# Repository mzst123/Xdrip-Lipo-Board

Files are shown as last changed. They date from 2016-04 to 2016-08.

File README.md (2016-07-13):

# Xdrip Lipo Bluetooth Board PCB
Xdrip on a printed circuit board!

The design files are in the folder ["Eagle PCB Files"](https://github.com/mzst123/Xdrip-Lipo-Board/tree/master/Eagle%20PCB%20Files)

Or you can order the PCB directly [here](https://oshpark.com/shared_projects/IuYnoGB9)

For other versions of this project check out the folder ["Other Versions"](https://github.com/mzst123/Xdrip-Lipo-Board/tree/master/Other%20Versions)

If you can't solder this board and need help send me an email and im sure we can figure something out. My e-mail address is my github username at gmail.com

## Features:

- The board uses a MAX1811 battery charging ic
- Both Xbridge & Xdrip circuit support, selectable via a switch
- Battery can be soldered directly on the PCB (2.54mm header) or via a JST-2 connector (2mm pitch)
- Charging Status LED (On = charging; off = full)

## Components:

- 3x 1206 SMD Resitors (150Ω, 10kΩ, 27kΩ)
- 2x 1206 SMD Capacitor 10μf
- 2x micro switch MSK-12C02
- 1x 1206 Red LED (any led should work)
- 1x micro usb socket (ebay id: 121829362799)
- 1x MAX1811 lithium charger IC
- 1x [JST-2 connector 2mm pitch](https://www.sparkfun.com/products/8612) (optional - your battery needs to have the mating connector - sparkfun sells compatible batteries, or buy the connector separately and crimp it on your battery)
- 1x HM-11 Bluetooth V4.0 Transceiver BLE Module (I got the one from fasttech)
- 1x Polulu Wixel
- 1x LiPo/Li-ion Battery (I recommend using a LiPo battery)

Attention! The MAX1811 Charger IC is set to 500mah. Only use a battery with more than 500mah.

I source most of my components from eBay because of the free shipping. Here are some example links but consider that the prices change daily and shipping depends on where you are located:
- [Resistors](http://www.ebay.com/itm/100pcs-1-4W-watt-1206-SMT-SMD-Chip-Resistor-from-0-ohm-to-10M-ohm-1-/252380762812?var=&hash=item3ac310d2bc:m:msXv_-i2Opl1RPDANdY3cMw)
- [Capacitors](http://www.ebay.com/itm/12pcs-1206-smd-tantalum-capacitor-16v-10uf-106-10-3216-a-type-ic-diy-develop-d1-/331840663464?hash=item4d433eafa8:g:MpYAAOSwubRXFXfc)
- [Micro Switch](http://www.ebay.com/itm/20-pcs-MSK-12C02-Mini-SPDT-1P2T-Slide-Switch-On-Off-SMD-7-Pin-For-MP3-MP4-/161857451517?hash=item25af74b5fd:g:e1IAAOSwl9BWHbT4)
- [Red Led](http://www.ebay.com/itm/10-x-1206-RED-Super-Bright-LED-Chip-SMD-SMT-Bulb-Lamp-Light-High-Brightness-RoHs-/191231419928?hash=item2c8647e618:g:O3sAAOSw9N1Vo3OF&vxp=mtr)
- [micro usb socket](http://www.ebay.com/itm/2015-New-10Pcs-Micro-USB-B-Female-5Pin-SMT-Socket-Connector-Hot-Sale-MO-/401091696043?hash=item5d62ed95ab:g:R2kAAOSwDNdVpfv5)
- [Max1811](http://www.ebay.com/itm/1PCS-USB-LI-CHARGER-IC-MAXIM-SOP-8-MAX1811ESA-MAX1811ESA-MAX1811ESA-T-/272041007390?hash=item3f56e8591e:g:rx0AAOSwAYtWPgb~)
- [LiPo battery](http://www.ebay.com/itm/3-7V-850mAh-Lipo-Polymer-li-ion-Battery-703040-for-cell-phone-Camera-DVD-GPS-PAD-/111909510772?hash=item1a0e539e74:g:FAoAAOSwFNZWxojb)
- [Bluetooth module(Fasttech)](https://www.fasttech.com/product/1740900-hm-11-bluetooth-v4-0-transceiver-ble-module)

## PCB Assembly:

Everything is labeled on the PCB. The components are large enough to be soldered by hand, the trickiest for me was the micro usb socket. But if you use a hot air rework station (40$ on ebay) it should be very easy.

Here is a video how-to:

IMAGE ALT TEXT HERE (http://www.youtube.com/watch?v=SYGwYvehjtA)

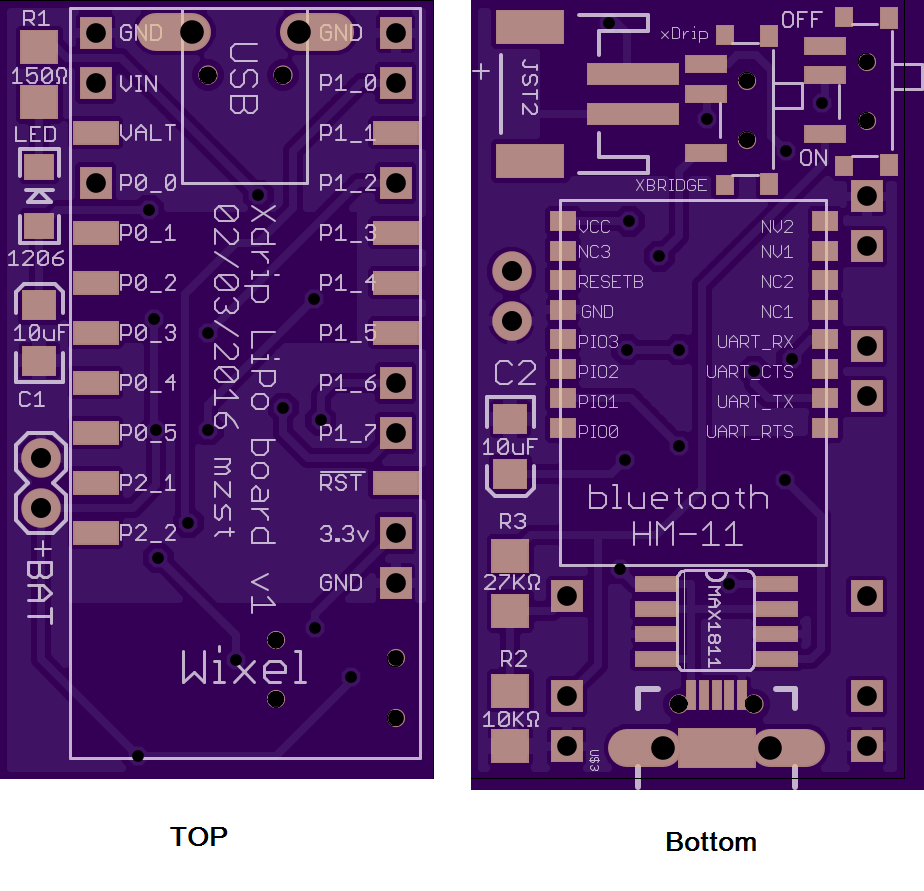
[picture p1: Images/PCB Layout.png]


## Schematics:

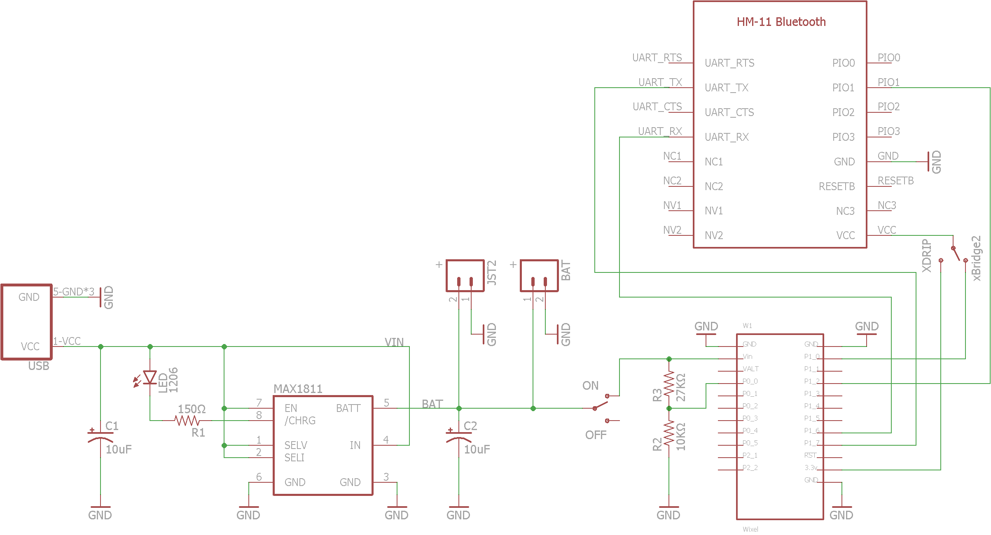
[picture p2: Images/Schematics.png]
Schematics


## Software:
For the Wixel software i recommend [xBridge](https://github.com/jstevensog/wixel-sdk/tree/master/apps/xBridge2) from [John] (https://github.com/jstevensog). Just download the .wxl file and load it to the wixel. There are many advantages of xBridge, for example you don't have to re-compile the program to change transmitters because you can set it inside the xDrip app, improoved power saving features, battery level estimate, etc...

[Here](https://github.com/StephenBlackWasAlreadyTaken/xDrip/wiki/xdrip-beta) you can download the latest xDrip android app.

## 3D Enclosure:

I made an enclosure, however it still has to be improved. To further reduce space, the JST-2 connector is not used in this design. In the future I might add one with JST-2 support. The battery compartment should fit an 850mah Lipo Battery (7x30x40mm). For more information and to download the .STL files go to the ["Enclosure"](https://github.com/mzst123/Xdrip-Lipo-Board/tree/master/Enclosure) Folder.
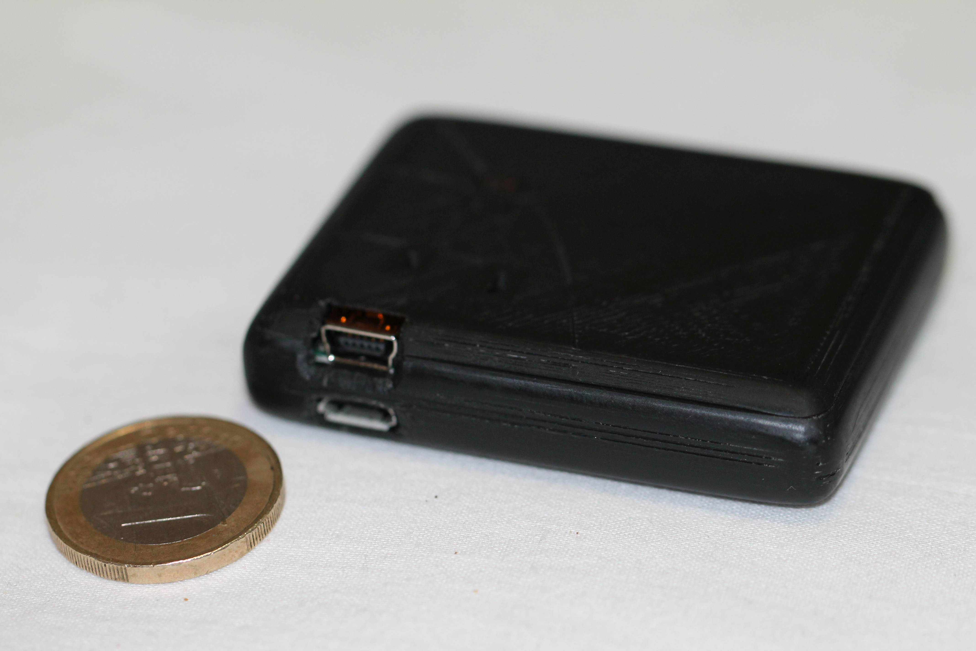
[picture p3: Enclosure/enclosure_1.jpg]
Enclosure


## Pictures:

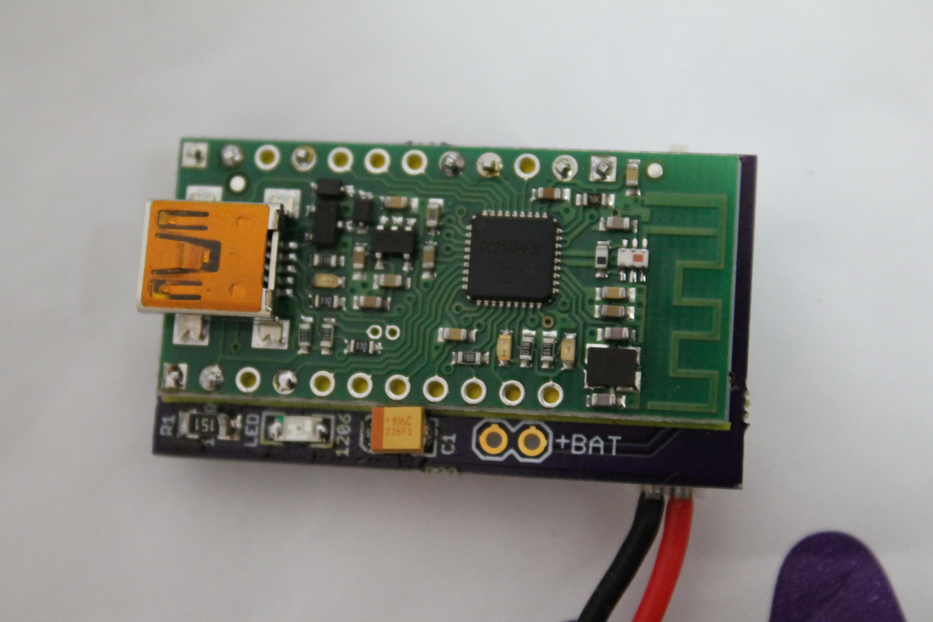
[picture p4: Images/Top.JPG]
Top View

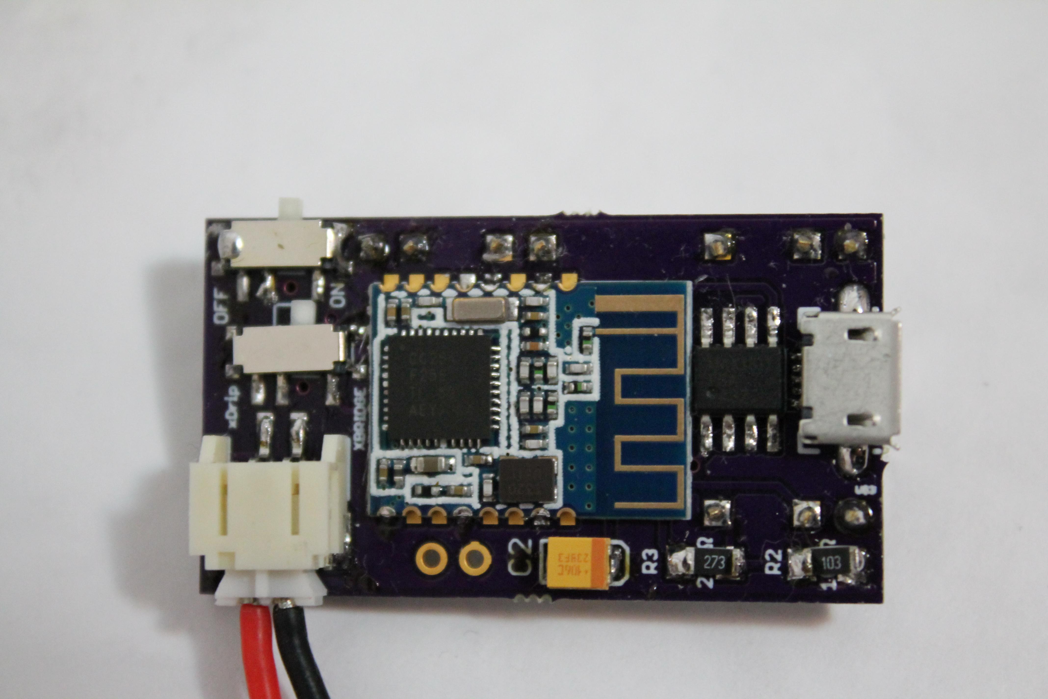
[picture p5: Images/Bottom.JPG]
Bottom View

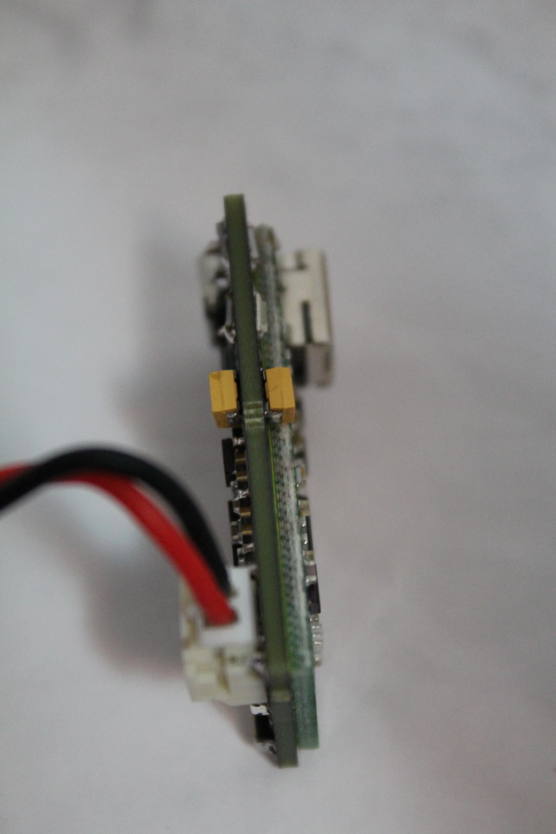
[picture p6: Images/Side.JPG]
Side View

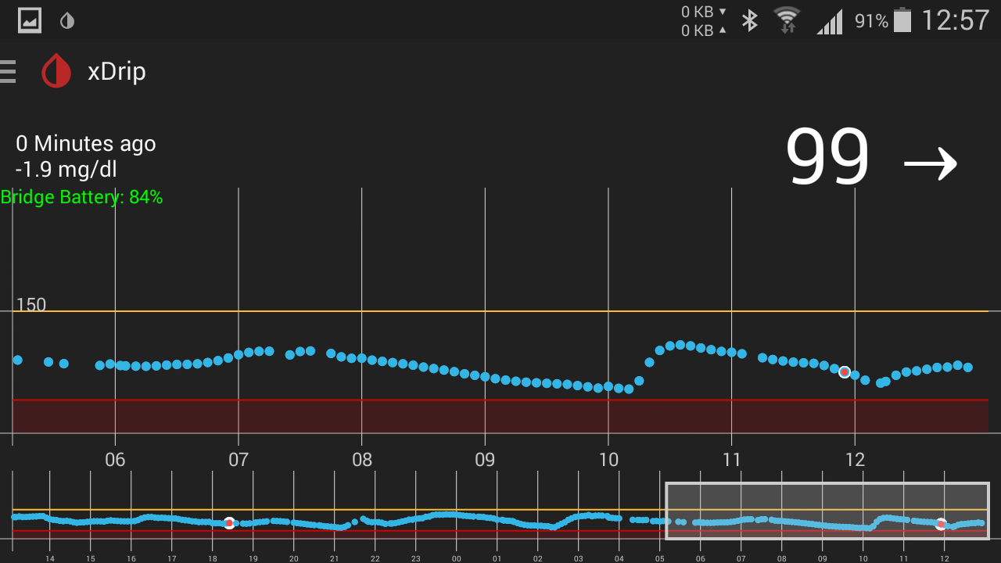
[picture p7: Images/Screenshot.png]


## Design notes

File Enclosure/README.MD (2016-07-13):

I made an enclosure, however it still has to be improved. To further reduce space, the JST-2 connector is not used in this design. In the future I might add one with JST-2 support. The battery compartment should fit an [850mah Lipo Battery](http://www.ebay.com/itm/3-7V-850mAh-703040-Lipo-Polymer-li-ion-Battery-for-cell-phone-Camera-DVD-GPS-PAD-/121844114909?hash=item1c5e79a5dd:g:LCwAAOSwUdlWdSaa) (7x30x40mm). 
I printed the parts on www.3dhubs.com for around 5€ shipped. The material used was PLA, but ABS is probably better.
Here are some pictures of the current progress:

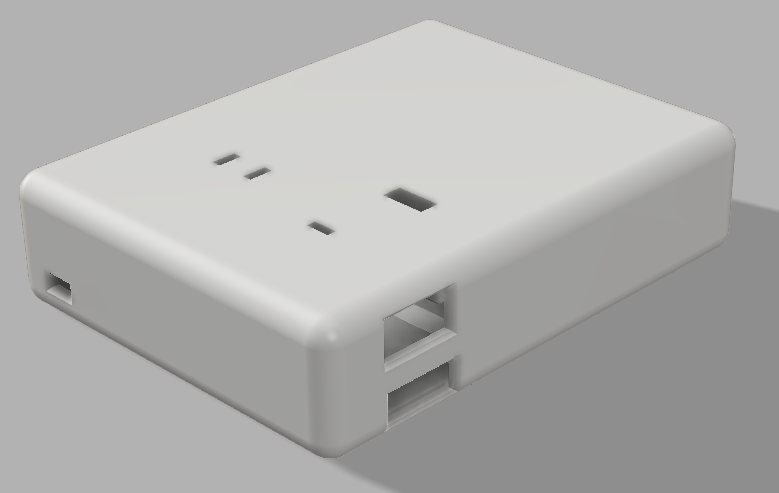
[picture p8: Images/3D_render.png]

Enclosure
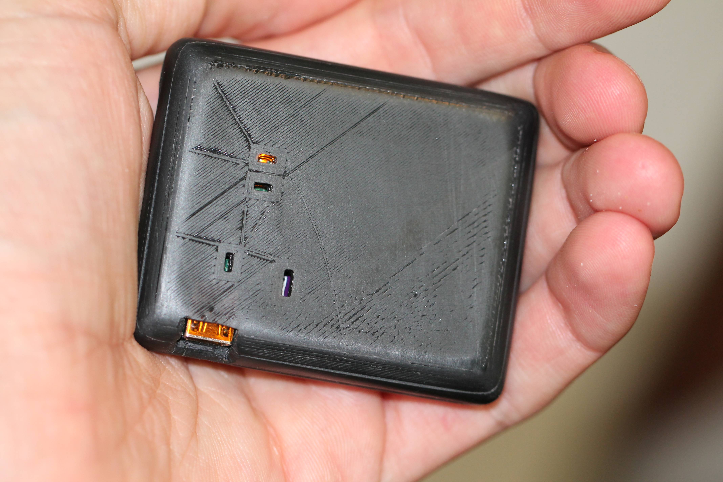
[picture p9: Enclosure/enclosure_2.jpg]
Enclosure

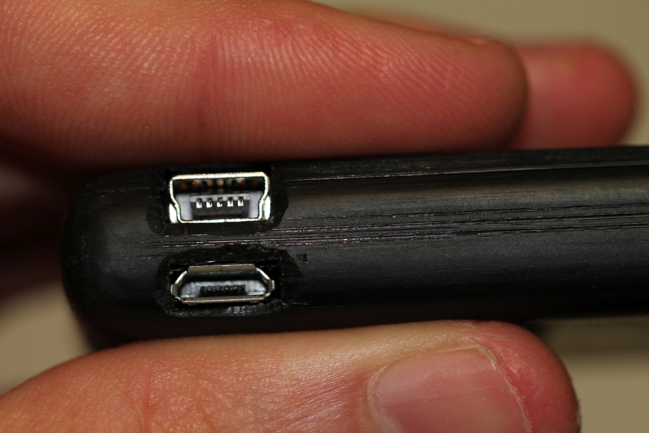
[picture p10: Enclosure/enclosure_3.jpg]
Enclosure

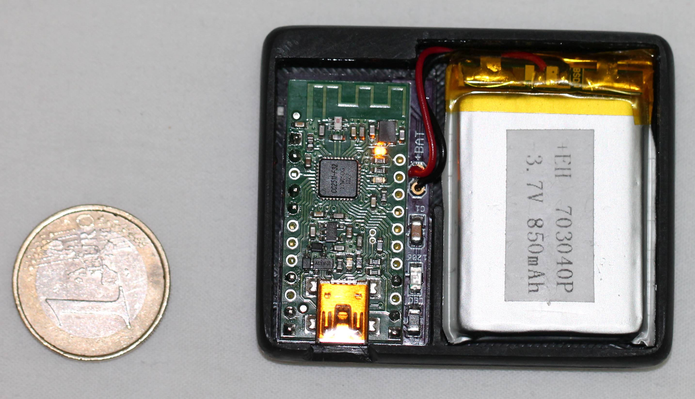
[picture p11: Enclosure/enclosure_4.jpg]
Enclosure


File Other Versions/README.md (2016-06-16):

# Other Versions

Here you will find other versions of the project.
- Currently there is only one for the [GSM/Parakeet Project](https://github.com/mzst123/Xdrip-Lipo-Board/tree/master/Other%20Versions/GSM-Parakeet)

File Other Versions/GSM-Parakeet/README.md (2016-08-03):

# GSM / Parakeet Version

# Tested & Works!
To order the PCB click [here](https://oshpark.com/shared_projects/pyIarV64).

This version uses a GSM module (SIM800L) instead of bluetooth. Check the [Parakeet project](https://jamorham.github.io/) for more info.

I had to switch to the TP4056 Charging IC because it has more power and is cheaper.

## Features:

- The board uses a TP4056 battery charging ic with a maximum charging power of 1000mA
- SIM800L Module sends the CGM data directly to the cloud
- Charging Status LED, Red = charging; Green = Full
- 4 ways to connect the battery: 
- - [JST-2 (sparkfun batteries, 2mm pitch)](https://www.sparkfun.com/products/341)
- - [JST-XH (ebay batteries, 2.54mm pitch)](http://www.ebay.com/itm/231387564843?_trksid=p2057872.m2749.l2648&ssPageName=STRK%3AMEBIDX%3AIT)
- - [2.54mm pitch screw-in connector](http://www.ebay.com/itm/2pcs-2-Poles-2-Pin-2-54mm-0-1-PCB-Universal-Screw-Terminal-Block-Connector-/262007114779?hash=item3d00d74c1b:g:5OIAAOSwPcVVwJQX)
- - Solder the wires directly

## Changelog
rev.1.0 - added JST-XH footprint, improoved pcb traces and vias

rev.0.9 - fixed SIM800L footprint, improoved pcb traces and vias

rev.0.8 - first version ready to manufacture

# Components

Most can be sourced from eBay

- SIM800L GSM Module
- 1x Polulu Wixel
- TP4056 Li Charging IC
- 2x 10μf Capacitors
- 1x 1.2kΩ Resistor (RPROG - 1.2kΩ=1000mA - Depends on Charging current - Check table below)
- 2x 330Ω Resistor
- 2x 1206 LED (1 Red and 1 Green)
- 1x [Micro USB Connector Female 4Legs](http://www.ebay.com/itm/10Pcs-Micro-USB-Type-B-Female-Socket-4-Vertical-Legs-For-Solder-Connectors-/351570406777?hash=item51db3aad79:g:UUwAAOSwu-BWOscw)
- 1x micro switch MSK-12C02
- 1x LiPo/Li-ion Battery (I recommend using a LiPo battery)
- 1x [JST-2 connector 2mm pitch](https://www.sparkfun.com/products/8612) (optional - your battery needs to have the mating connector - sparkfun sells compatible batteries, or buy the connector separately and crimp it on your battery)
- 1x JST-XH 2-pin connector (optional - only if your battery has this type of connector or you plan on crimping your own)

# Setting the charging current

You can individually set the charging current. Just change the RPROG resistor to the value you want.
The charging Current should be set dependent on the battery used. Always use a charging current equal or lower than the battery capacity.

|RPROG (kΩ)|IBAT(mA)| 
|:--------:|:------:|
|10        |130     |
|5         |250     |
|4         |300     |
|3         |400     |
|2         |580     |
|1.66      |690     |
|1.5       |780     |
|1.33      |900     |
|1.2       |1000    |

## Schematics:

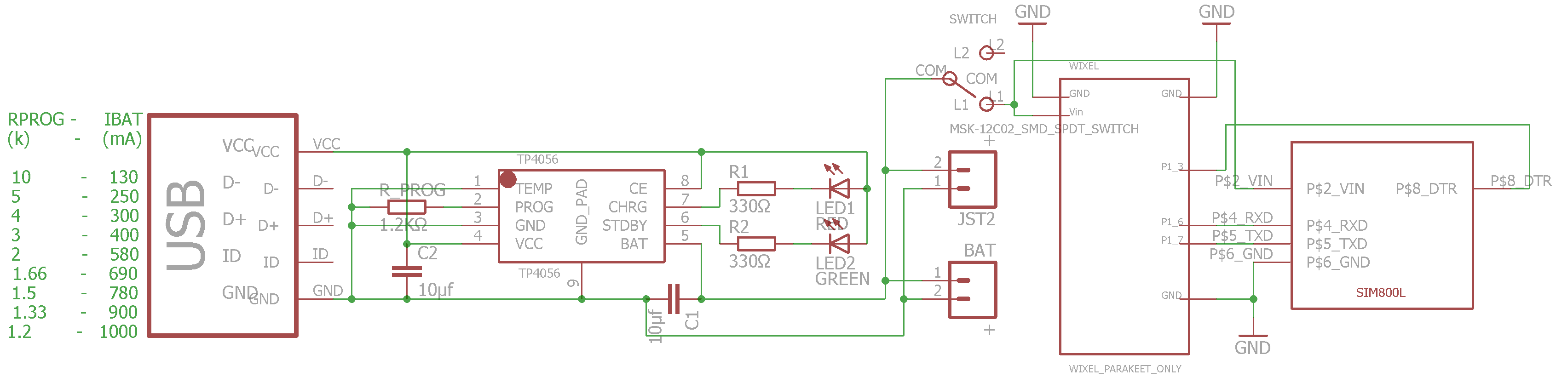
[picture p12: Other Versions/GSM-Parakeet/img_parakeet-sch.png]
Schematics


## Pictures:

Top View

Bottom View

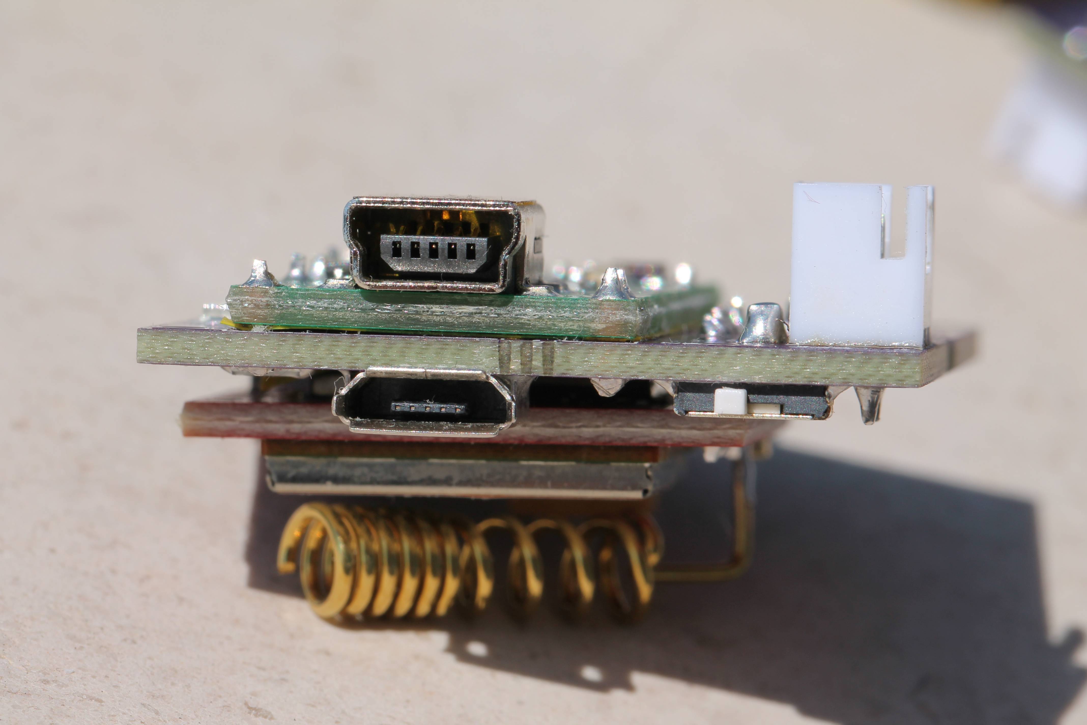
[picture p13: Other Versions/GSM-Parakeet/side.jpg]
Side

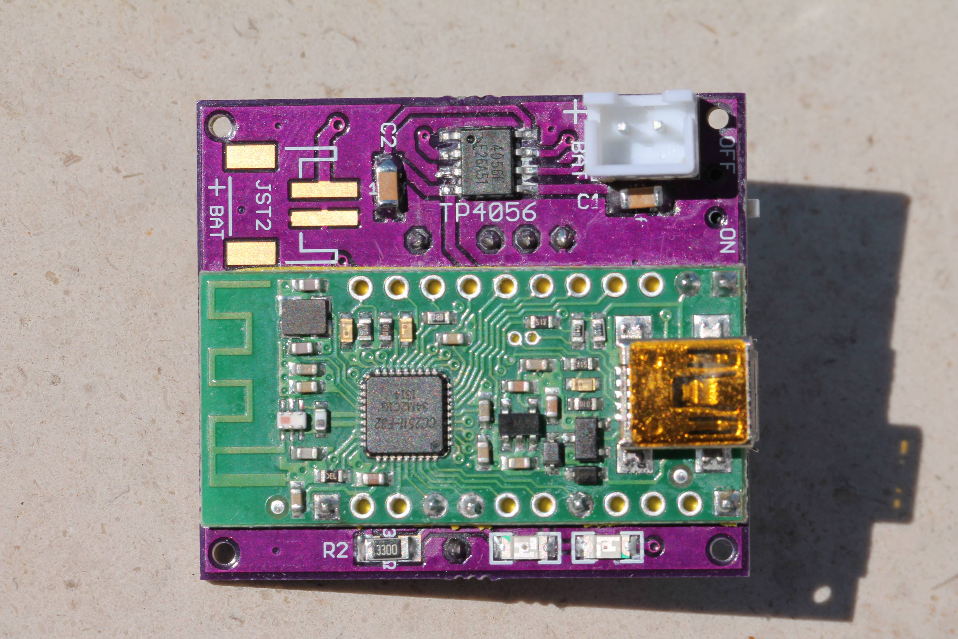
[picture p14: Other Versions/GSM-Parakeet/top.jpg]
Top

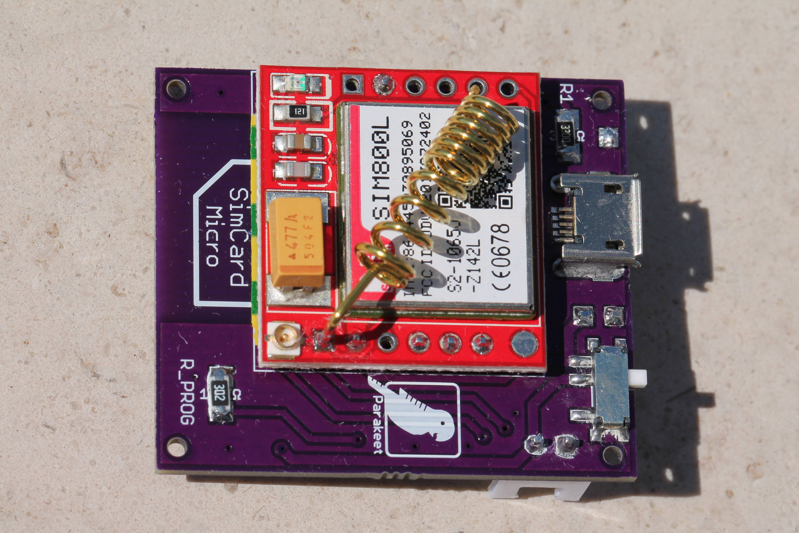
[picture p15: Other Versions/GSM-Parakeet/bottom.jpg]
Bottom

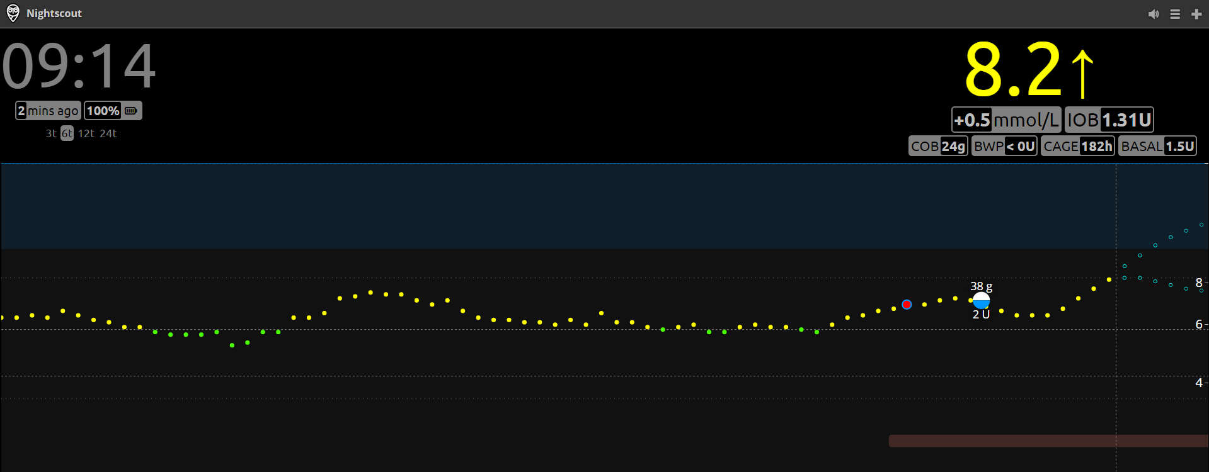
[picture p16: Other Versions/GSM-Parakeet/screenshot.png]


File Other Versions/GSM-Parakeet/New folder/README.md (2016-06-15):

# GSM / Parakeet Version

# Experimental Version - has not been tested yet
To order the PCB click [here](https://oshpark.com/shared_projects/lI7P3ltc).

This version uses a GSM module (SIM800L) instead of bluetooth. Check the [Parakeet project](https://jamorham.github.io/) for more info.

I had to switch to the TP4056 Charging IC because it has more power and is cheaper.

# Components

- SIM800L GSM Module
- 1x Polulu Wixel
- TP4056 Li Charging IC
- 2x 10μf Capacitors
- 1x 1.2kΩ Resistor (RPROG - 1.2kΩ=1000mA - Depends on Charging current - Check table below)
- 2x 330Ω Resistor
- 2x 1206 LED (1 Red and 1 Green)
- 1x Micro USB Connector Female 4Legs
- 1x micro switch MSK-12C02
- 1x LiPo/Li-ion Battery (I recommend using a LiPo battery)
- 1x JST-2 connector (optional - your battery needs to have the mating connector - sparkfun sells compatible batteries, or buy the connector separately and crimp it on your battery)

# Setting the charging current

You can individually set the charging current. Just change the RPROG resistor to the value you want.
The charging Current should be set dependent on the battery used. Always use a charging current equal or lower than the battery capacity.

|RPROG (kΩ)|IBAT(mA)| 
|:--------:|:------:|
|10        |130     |
|5         |250     |
|4         |300     |
|3         |400     |
|2         |580     |
|1.66      |690     |
|1.5       |780     |
|1.33      |900     |
|1.2       |1000    |

## Schematics:

Schematics

## Pictures:

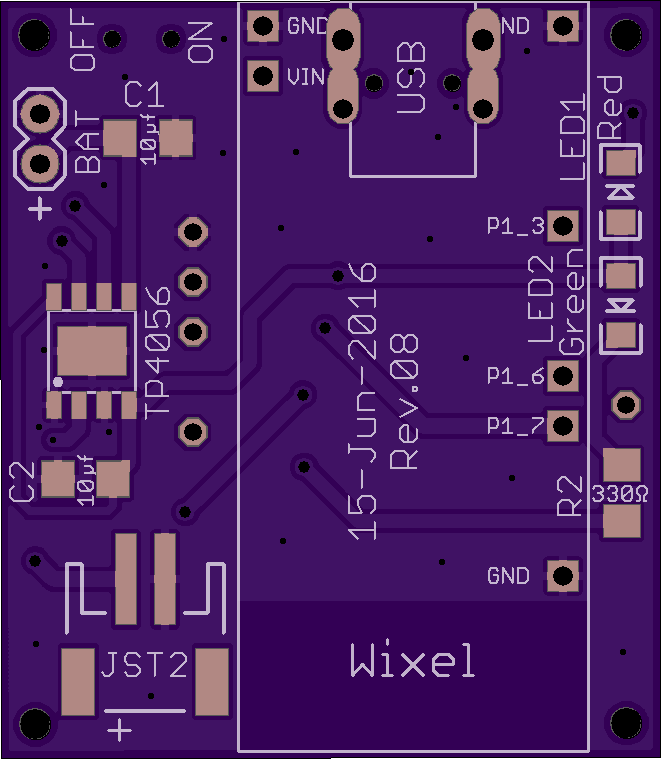
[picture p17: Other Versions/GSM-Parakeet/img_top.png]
Top View


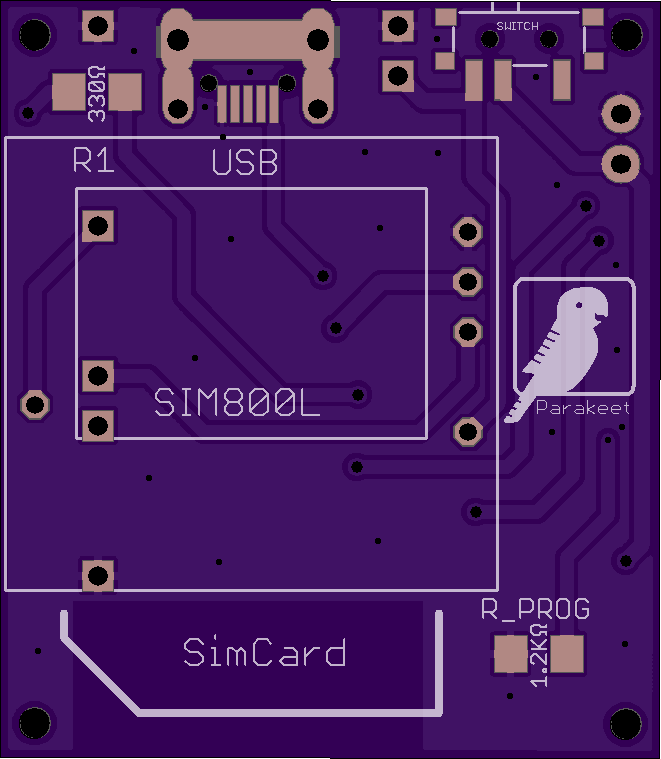
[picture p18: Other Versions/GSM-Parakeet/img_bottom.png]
Bottom View


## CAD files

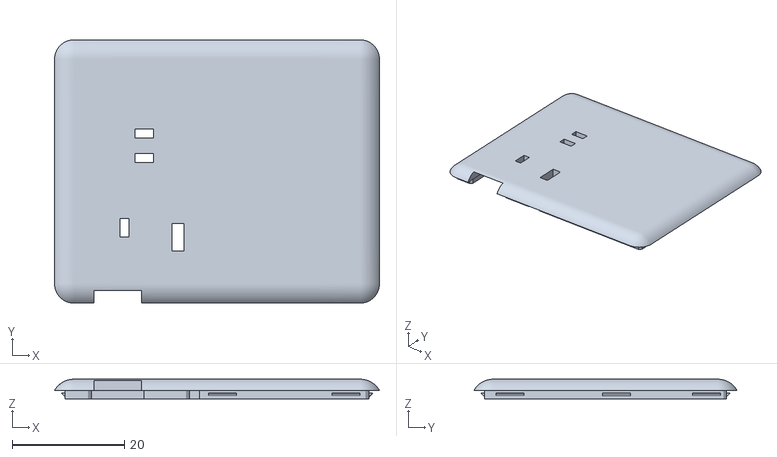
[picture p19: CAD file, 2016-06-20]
Enclosure/STL files/Top.stl
57.9 x 46.9 x 3.50

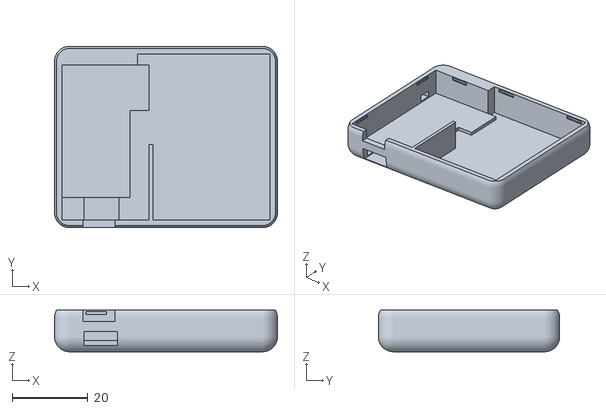
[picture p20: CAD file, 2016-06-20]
Enclosure/STL files/Bottom.stl
59.0 x 48.0 x 11.0

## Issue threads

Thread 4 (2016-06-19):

### ISSUE TITLE
GSM PCB

### ISSUE THREAD

**Issue by runeron** [mzst123/Xdrip-Lipo-Board#4]
First of all, thank you for this; excellent having a PCB to solder the components on.

Now that I have a working BLE receiver, I am planning to create a GSM receiver/[Parakeet](https://github.com/jamorham/wixel-xDrip/blob/parakeet-gsm-modem/README.md). What are the chances of you creating a modified version of this PCB where the HM11 is replaced by the SIM800L GSM module?

I would do it myself, but then I have to teach myself HOW first...

**Comment by mzst123** [comment]
Hi, it sure seems very easy. The only problem is that there is no footprint available. I do not have a SIM800L module. Can you measure the holes of the module and make a drawing? Then I can copy it into the program.
I need to do something like this so only the distances of the holes and the outline of the module are relevant. Regards
![tp4056 module](https://cloud.githubusercontent.com/assets/16510934/15784499/b0c4566e-29aa-11e6-8a05-74ac352b6b8c.png)

**Comment by runeron** [comment]
Outer dimension of module: 2.5 cm x 2.3 cm (Thickness is x 0.7 cm). The holes are made for pin headers w/2.5 mm pitch. Drawing is best effort..
![sim800l](https://cloud.githubusercontent.com/assets/3177490/15791790/bd39378c-29d9-11e6-98f1-7337ec182b2b.png)
Not sure how it would be solved to have it on the PCB, but since there are components on both sides, maybe just have holes for the 6 x 1 & 5 x 1 pin headers (2.5 mm pitch) on each side of the SIM800L board?

**Comment by mzst123** [comment]
Thanks i will see what i can come up with. Only one measurement is missing: the distance between the hole and the edge of the PCB.
![untitled](https://cloud.githubusercontent.com/assets/16510934/15802480/a504b286-2aab-11e6-95c0-6b06b9b27a35.png)

**Comment by runeron** [comment]
Nice.. It's 1,5 mm as far as I can measure.

Edit: The measurements in my earlier sketch was from center-hole. Just thought I'd mention it

**Comment by mzst123** [comment]
Hi, I just made this draft. Please print this out on an sheet of A4 paper. If you can, use a laser printer on maximum resolution setting. Then place the module on top an check if it fits. You can also stick the header pins into the paper and see if they fit. 
The sim tray is on the back (in contact with the paper).
Thanks
[SIM800L-.pdf](https://github.com/mzst123/Xdrip-Lipo-Board/files/303821/SIM800L-.pdf)

**Comment by runeron** [comment]
Amazing! I will try it out as soon as I get back from work today.

I did notice a potential challenge yesterday, though.. It doesn't look like the SIM800L will work with the 3.3V from Wixel (requires 3.4V~4.4V & 2A at peak):

![image](https://cloud.githubusercontent.com/assets/3177490/15887249/8a6cdba2-2d61-11e6-82c5-7e904d6ce6e0.png)

I did all the connections on my breadboard; just replacing the HM11 w/GSM, and was not able to communicate with it. After doing som more reading, it appears the Wixel is not able to wake up the SIM module.

I tried connecting the SIM800L directly to the powersource (first 500mAH, 3.7V Li Po (25C), then 2400mAH, 3.7V Li Ion battery) with no success. I think I might need another powersource, and I also think the SIM800L needs to be powered directly from source; I guess this would require additional modifications of the PCB.

It COULD be the simcard (provider/defect/etc), but ran out of time yesterday; I was also struggling with figuring out the meaning of the different the LED statuses I got. Will try more today if I manage to find the time, and will try powering w/batteries as suggested in jamorham's parakeet guide.

It is a bit more work than I thought.. Still; if you make the Eagle model of SIM800L that would be fantastic.. Then I can eventually try and make a PCB myself if this is too much work for you :)

**Comment by runeron** [comment]
Hi, and sorry for the delay!

I matched up the pins as best I could, and it looked like it was a perfect fit.

I've had a look at your eagle files, and I can order the parts and try this out whenever you feel it is ready. No problem if it doesn't work on the first try.

My only issue is deliverytime of PCB boards; I might need to find a quicker way of getting them made.

**Comment by mzst123** [comment]
Perfect. I made the board as a test. I still have to move some components for better access to the simcard, as i don't know how much space there will be to insert it. During next week it will be ready ;). I changed some of the components (lessons learned from the old board). Can you solder the smaller components?
If not, i could help you assembling the boards. I bought a hot air rework station, so let me know.

**Comment by runeron** [comment]
I did struggle a bit with a few components on the last board, but I am waiting for some solder paste now; hoping this will help..

Not sure how you could assist in assembling, as I live in Norway. Otherwise that would be great:)

**Comment by mzst123** [comment]
Well I could order the parts, assemble the boards and mail them to you. Its not a problem for me, however it will take a little longer.

**Comment by runeron** [comment]
Wow. That would be amazing.. I can transfer money for parts/work via paypal or whatever you prefer, if you pm me the details.

Edit: removed

Not sure how that is possible on github, so will leave my email here for now. :)

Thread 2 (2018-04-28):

### ISSUE TITLE
Little Help Needed here in Canada

### ISSUE THREAD

**Issue by Tatt2edone** [mzst123/Xdrip-Lipo-Board#2]
I have ordered the boards from OSH Park, I am currently looking for all the parts needed, my question involves the micro switches, are they a must? I currently have an xDrip Wireless Bridge built, there are no switches, its always on. I get the on/off switch option, but what is the difference between xdrip circuit and xbridge circuit? 

I am sorry if this is a dumb question, just don't want to mess this up.

**Comment by mzst123** [comment]
Hello, switches are not a must, but I have them because if you choose to solder on the battery permanently, you have no way to reboot or turn off the device, for troubleshooting etc... 
If you don't want to use the switches, just bridge the contacts with a little wire and solder.
There are two circuits, wich vary only slightly. 
The original **xDrip** project used a circuit, wich was then further improved by John (jstevensog) and called **xBridge**.
He changed the [Wixel Program](https://github.com/jstevensog/wixel-sdk/tree/master/apps/xBridge2) to perform better and more efficient, and to show an approximate battery level value. You also don't have to compile the program each time you switch transmitters, because you can set the Transmitter ID from within the xDrip app. You can use this Wixel Program with both circuits, but the power saving features only work with the xBridge circuit.
Its up to you wich one you prefer, and with the switch you can easily test wich one works better for you. Another advantage is that the xBridge Wixel Program continues to be updated and improved to this day.
I personally use the xBridge circuit. 
As a side note, make sure you buy the exact micro-usb socket type as indicated, as there are many different versions and not all of them fit the layout perfectly.

Regards and good luck, if you have any questions ask away.

**Comment by Tatt2edone** [comment]
Thanks for the reply, I used the xDrip UK site to auto compile the wixel program for xDrip, but I think I will look into xBridge, 
Is this usb the correct one?

http://www.digikey.ca/scripts/DkSearch/dksus.dll?Detail&itemSeq=197088528&uq=635986860270805947

This company has all the parts listed and are in Canada so I don't have to worry about crazy exchange rates and long shipping times.

One last thing for now, I checked out the xBridge github, I am very new to this stuff, I am on my own building this stuff for my wife and just want to get it right for her. Can I just download the wixel file, reprogram my current xDrip box?

We are using the most current beta of xDrip, will it recognize the xBridge wixel program?

**Comment by mzst123** [comment]
Hi, unfortunately the link doesn't return a valid result. [This one](http://www.digikey.ca/product-detail/en/amphenol-fci/10118192-0001LF/609-4613-2-ND/2785387) should work, however it is not the one i used (cant find it on this site). The one i used has two little plastic legs that will fit the holes in the PCB, but for functionality it is not important, it just makes placing the part easier. If you are going to Reflow the board it doesn't matter, both will work fine.
About the xBridge, yes. Just download the .wxl file and load it on to the wixel. It should set itself up in a few minutes, watch the LEDs blinking, it is described in the PDF. You don't have to do anything. Just pair the device with the phone (I think HM-11 default pin is 000000 (six zeroes)) and xDrip should recognize the wixel just fine. Then enter the Transmitter ID. That's it. Regards

**Comment by Tatt2edone** [comment]
Hey, back again, I talked with digi-key about getting a jst-2 connector, apparently there are many variations in spacing for the pins. Do you remember what the spacing of the one you used? What type was it, right angle, flat (if there's such a thing) etc?

Thanks for your patience and help, I received shipping notice from OSH that the boards are on their way.

**Comment by mzst123** [comment]
Hey, [This is the one i used](https://www.sparkfun.com/products/8612) but i bought it from element14 as i am from europe. I bought all the other components from eBay with free shipping. Took over a month to arrive though. This connector is not strictly necessary as you can solder the battery directly on board if you can't source it. It is also quite expensive, that's why i left it optional. Digikey is very expensive on shipping. Regards
Edit: I forgot to add, they are the 2mm (header, smt) variant. Cheers

**Comment by mzst123** [comment]
I forgot to add, they are the 2mm (header, smt) variant. Cheers

**Comment by Tatt2edone** [comment]
Much appreciated! I will see what my area's supplier has. Cheers to you as well! DigiKey is only $8 shipping for all the parts I am ordering, everything needed in addition to what I have is there. I have 2 wixels, a bunch of hm-10 and a bunch of hm-11 on the way, I realize the hm-10 won't fit, but have them for old school xDrip builds in a pinch :)

**Comment by apabari** [comment]
Hello!  Tatt2edone, wondering -- do you have a parts list for the digikey order that you could post/share?  I'm also in Canada, and interested in ordering the components (and a board from OSHPark) -- just a little lost on the digikey website.

**Comment by apabari** [comment]
Just checking in!  Could anyone post the parts list for getting the components from digikey?

**Comment by mzst123** [comment]
Hey, its easier if you buy from eBay... lower prices because you can buy lower quantities... Didn't i send you a board some time ago? What happened?

**Comment by apabari** [comment]
I never received the board.  Lost our original e-mail thread so I didn't reach out again.  Do you have the tracking number? I'd love to try and find out what happened to it!

I ordered the components from e-bay and built one, but I'm pretty sure I ordered the wrong resistors and capacitors... it didn't work.  If you could point me at the product codes from digikey that would be great.  They do next day shipping and it's pretty inexpensive to order from them here in Toronto.

**Comment by mzst123** [comment]
So it was you. I wasn't sure. The board was returned to my address with a notice that it was delivered but not accepted. Im not sure if i still have the tracking number but it has probably expired anyway. Since you never reached out I forgot about it. I will look up the codes later today

**Comment by apabari** [comment]
That's really strange!  I am very disappointed to hear that.  If you could refund me the cost (less shipping, of course) I would really appreciate that as well.  Thanks for your help with finding the codes!

**Comment by mzst123** [comment]
Just sent you a refund! Here are some parts, if you need more help let me know:
[10KΩ resistor](http://www.digikey.pt/product-detail/en/yageo/RC1206FR-0710KL/311-10.0KFRCT-ND/731430)
[27kΩ Resistor](http://www.digikey.com/product-detail/en/yageo/RC1206FR-0727KL/311-27.0KFRCT-ND/731679)
[150Ω resistor](http://www.digikey.com/product-detail/en/yageo/RC1206JR-07150RL/311-150ERCT-ND/732170)
[10μf Capacitor](http://www.digikey.pt/product-detail/en/yageo/CC1206ZKY5V7BB106/311-1376-2-ND/2103114)
[LED](http://www.digikey.com/product-detail/en/kingbright/APT3216SURCK/754-1143-2-ND/1747542)

**Comment by apabari** [comment]
Thank you!  Just ordered the parts from Digi-Key.  Thanks so much for all of your continued help - hope this works out for me!

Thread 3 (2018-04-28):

### ISSUE TITLE
New to T1 & looking at getting set up

### ISSUE THREAD

**Issue by Deneil1983** [mzst123/Xdrip-Lipo-Board#3]
Morning I'm new to T1 Diabeties, my 5yr old daughter has been resently diagnosed. Be been trying to work out what's the best method for Xdrip while Mariella is at school. I've ordered the newest version of the PCB Xdrip board, wixel, HM11 but as far as anything else goes I haven't got a clue were or what there for. We're do I get the info to download the wixel? And could you post links were to get the rest of the components that I would need to get. I'm in the UK so anywere UK or Europe based would be a help xxx

**Comment by runeron** [comment]
Hello. I would suggest you read the following:
- [Nightscout](http://www.nightscout.info/)
- [xDrip](http://stephenblackwasalreadytaken.github.io/xDrip/)

Regarding the PCB blueprints posted here, they are for creating an additional/alternative Dexcom receiver. All components are listed on this site as well (and also the wiring diagram, for your question regarding the other components). It is marked on the PCB where each component goes. Personally I have used the following sites for ordering: eBay, SparkFun, HobbyTronics

NOTE: xBridge and xDrip are essentialy the same, but xBridge circuit has some additional functionality (at least that is how I understand it). Some of the "additional" components are only required if you use the xBridge setting (?).

My reasons for creating this board (still waiting for components):
- Monitor our 3 yr old (T1 for 6 months) even when he's in kindergarden/visiting others
- Use smartphones instead of the Dexcom receiver
- Uses "better" algorithm for calculating sender measurements, compared to the outdated Dexcom EU software

I would also sugges you check out the site listed below, which has instructions for creating a receiver to upload data to the "cloud" without need for an android phone:
- [Parakeet](http://jamorham.github.io/)

Best of luck!

**Comment by mzst123** [comment]
@runeron Yes that is exactly how it works. The only additional components the xBridge needs are two resistors to estimate battery level.

@Deneil1983 I have sourced almost all components from eBay, as the shipping is free (it takes a month to arrive from China or HongKong though). For example, for the LED, just go to `ebay.com` and enter `1206 Red LED`. Then you sort by `Price + Shipping: lowest first`and click on only show `Buy it now` results. Now scroll down a little until you find one result that you want, for example i got [this one](http://www.ebay.com/itm/10-x-1206-RED-Super-Bright-LED-Chip-SMD-SMT-Bulb-Lamp-Light-High-Brightness-RoHs-/191231419928?hash=item2c8647e618:g:O3sAAOSw9N1Vo3OF&vxp=mtr).
For $0.80 you get 10 Leds shipped to your house, no additional charges. Quite Cheap considering that on most other electronic websites you have to pay over 5€ in shipping. Now do the same process for all the other components. Here are some example links but consider that the prices change daily and shipping depends on where you are located (I live in Portugal). If you don't want to wait that long then order from a local supplier, for the UK i think Farnell/Element14 is good but expensive.
- [Resistors](http://www.ebay.com/itm/100pcs-1-4W-watt-1206-SMT-SMD-Chip-Resistor-from-0-ohm-to-10M-ohm-1-/252380762812?var=&hash=item3ac310d2bc:m:msXv_-i2Opl1RPDANdY3cMw)
- [Capacitors](http://www.ebay.com/itm/12pcs-1206-smd-tantalum-capacitor-16v-10uf-106-10-3216-a-type-ic-diy-develop-d1-/331840663464?hash=item4d433eafa8:g:MpYAAOSwubRXFXfc)
- [Micro Switch](http://www.ebay.com/itm/20-pcs-MSK-12C02-Mini-SPDT-1P2T-Slide-Switch-On-Off-SMD-7-Pin-For-MP3-MP4-/161857451517?hash=item25af74b5fd:g:e1IAAOSwl9BWHbT4)
- [Red Led](http://www.ebay.com/itm/10-x-1206-RED-Super-Bright-LED-Chip-SMD-SMT-Bulb-Lamp-Light-High-Brightness-RoHs-/191231419928?hash=item2c8647e618:g:O3sAAOSw9N1Vo3OF&vxp=mtr)
- [micro usb socket](http://www.ebay.com/itm/2015-New-10Pcs-Micro-USB-B-Female-5Pin-SMT-Socket-Connector-Hot-Sale-MO-/401091696043?hash=item5d62ed95ab:g:R2kAAOSwDNdVpfv5)
- [Max1811](http://www.ebay.com/itm/1PCS-USB-LI-CHARGER-IC-MAXIM-SOP-8-MAX1811ESA-MAX1811ESA-MAX1811ESA-T-/272041007390?hash=item3f56e8591e:g:rx0AAOSwAYtWPgb~)
- [LiPo battery](http://www.ebay.com/itm/3-7V-850mAh-Lipo-Polymer-li-ion-Battery-703040-for-cell-phone-Camera-DVD-GPS-PAD-/111909510772?hash=item1a0e539e74:g:FAoAAOSwFNZWxojb)

For the Wixel software i recommend [xBridge](https://github.com/jstevensog/wixel-sdk/tree/master/apps/xBridge2) from [John](https://github.com/jstevensog). Just download the .wxl file and load it to the wixel. There are many advantages of xBridge, for example you don't have to re-compile the program to change transmitters because you can set it inside the xDrip app. Regards

**Comment by Deneil1983** [comment]
Thank you for all your help, I think I've managed to get everything. Could you just double check these links to make sure there all correct before I go and buy them please?

https://www.ebay.co.uk/ulk/itm/121966808792 

https://www.ebay.co.uk/ulk/itm/391293464671 

https://www.ebay.co.uk/ulk/itm/361517418457 

https://www.ebay.co.uk/ulk/itm/321604978839 

https://www.ebay.co.uk/ulk/itm/261474884369 

https://www.ebay.co.uk/ulk/itm/191794514614 

https://www.ebay.co.uk/ulk/itm/151637924468

**Comment by mzst123** [comment]
Yes that looks good. Let me know when you finish it. Cheers

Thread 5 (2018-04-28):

### ISSUE TITLE
Parakeet

### ISSUE THREAD

**Issue by Deneil1983** [mzst123/Xdrip-Lipo-Board#5]
Hi have you had any joy getting the parakeet to work? I've ordered the parts but as yet not been able to older them all together, is there anyway you would be able to help me build the parakeet if I was to send you all the stuff. 

Thanks
Deneil

**Comment by mzst123** [comment]
Sure thing. It works. I can help you, no problem. Please contact me via e-mail

**Comment by Deneil1983** [comment]
Your a life saver, will email you now thanks

**Comment by Deneil1983** [comment]
Hi thank you so much for agreeing to help me get set up with the parakeet. What would be the best way for you to help me get set up? I send you what I already have or you make it and I cover the costs for materials? I'm ok with both suggestions.

Thanks once again 
Deneil xxx

Deneil Yates-Savage 💗

Wednesday, 3 August 2016, 2:16 pm +0100 from notifications@github.com  notifications@github.com:

**Comment by Deneil1983** [comment]
Hi can you send.me.your email address xxx

**Comment by mzst123** [comment]
Hi, i think it is easier if you send me what you already have.

**Comment by Deneil1983** [comment]
Email sent thank you so much

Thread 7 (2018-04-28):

### ISSUE TITLE
Enclosure - different size batteries?

### ISSUE THREAD

**Issue by whoiswes** [mzst123/Xdrip-Lipo-Board#7]
mzst123,

First, thank you for putting both the PCB and enclosure projects together - I have built 2 boards so far and they have performed fantasic!

I do however wonder if it would be possible to have additional enclosures designed for larger batteries.  Currently I'm using a 2000 mAh battery from adafruit in a tic-tac case.  It's functional, but larger.  I'd be happy to design a case around the larger battery size, but am unsure where to start in terms of design tools  I have zero 3D printing experience.

My apologies for putting this on the bug tracker as a discussion rather than an actual bug, but hopefully this will spawn some useful discussion, if nothing else.

Again, thank you so much for making this available

Wes

**Comment by mzst123** [comment]
Hi, i used the free program "Autodesk Fusion 360" to design the cases but im sure there are better ways to do it. It works but has some annoyances. I also had no experience in 3D design before. I made an updated version from the mistakes learned (but with same size battery) that i haven't published yet. The biggest problem I encountered was with the tolerances of the material/printer. Another issue was the closing mecanism which is not possible to do reliably with the material i used (PLA) so now i just close it with some adhesive tape.
I can upload the files if you want.
Regards

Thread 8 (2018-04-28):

### ISSUE TITLE
Version V2.1

### ISSUE THREAD

**Issue by d3xr** [mzst123/Xdrip-Lipo-Board#8]
Hi! Where I can find Xdrip PCB Lipo Board V2.1 files?

**Comment by mzst123** [comment]
Hi, the files are [here](https://github.com/mzst123/Xdrip-Lipo-Board/tree/master/Eagle%20PCB%20Files). you can also order them directly from [OSHPark](https://oshpark.com/shared_projects/IuYnoGB9). Regards

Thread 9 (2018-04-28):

### ISSUE TITLE
Help from an expert needed

### ISSUE THREAD

**Issue by Stef-M** [mzst123/Xdrip-Lipo-Board#9]
Hi,
i've read about this wonderful project, and am very interested.
I'd like to ask you if you have considered to sell one (eg if you have one more circuit).
Unfortunately I'm not so expert for realizing one from scratch.

Many thanks in advance.

Best regards :)

**Comment by mzst123** [comment]
Hi, I think I should still have one or two at home. I will check and let you know tomorrow. Regards

**Comment by mzst123** [comment]
Hi @Stef-M 
I just checked and i still have parts to build at least one. Only the Bluetooth module is missing, but i could order it for you. Let me know if you are still interested.
Regards

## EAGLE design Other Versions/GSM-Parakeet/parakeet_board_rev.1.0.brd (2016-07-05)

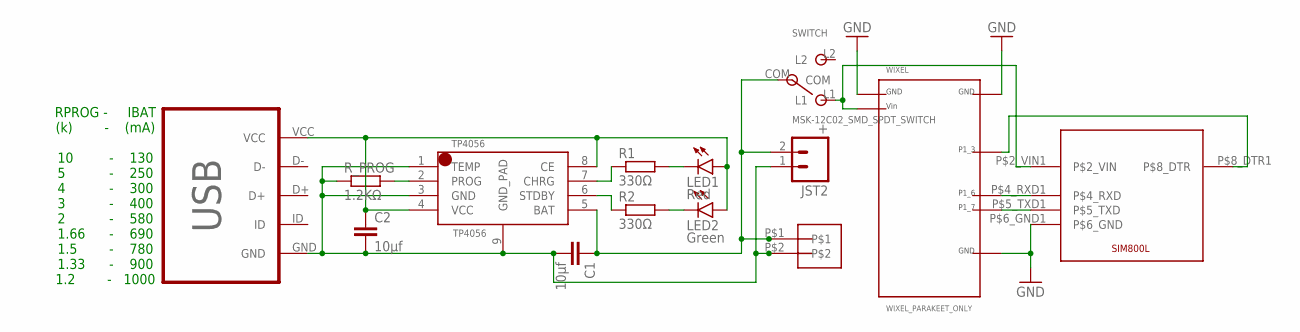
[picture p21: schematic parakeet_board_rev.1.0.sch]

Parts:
C1, C2: 10μf; C1206
JST2: +; JST-2-SMD
JST-XH: 2_PIN_JST-XH-B2B
LED1: Red; LED-1206
LED2: Green; LED-1206
R1, R2: 330Ω; R1206
R_PROG: 1.2KΩ; R1206
SIM800L: SIM800L_PARAKEET_ONLY
SWITCH: MSK-12C02_SMD_SPDT_SWITCH; MSK-12C02
TP4056: TP4056; SOP-8
USB: MICRO-USB-B; MICRO_USB_4_LEGS
WIXEL: WIXEL_PARAKEET_ONLY

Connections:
GND: C1.2, C2.2, JST2.1 (2), JST-XH.P$2, R_PROG.1, SIM800L.P$6_GND1 (P$6_GND), TP4056.1 (TEMP), TP4056.3 (GND), TP4056.9 (GND_PAD), USB.GND, WIXEL.P$1 (P$1-GND1), WIXEL.P$12 (P$12-GND2), WIXEL.P$23 (P$23-GND3)
unnamed: R_PROG.2, TP4056.2 (PROG)
unnamed: SIM800L.P$5_TXD1 (P$5_TXD), WIXEL.P$20 (P$20-P1_7)
unnamed: LED1.C, R1.2
unnamed: LED2.C, R2.2
unnamed: R1.1, TP4056.7 (CHRG)
unnamed: R2.1, TP4056.6 (STDBY)
unnamed: C2.1, LED1.A, LED2.A, TP4056.4 (VCC), TP4056.8 (CE), USB.VCC
unnamed: C1.1, JST2.2 (1), JST-XH.P$1, SWITCH.COM, TP4056.5 (BAT)
unnamed: SIM800L.P$4_RXD1 (P$4_RXD), WIXEL.P$19 (P$19-P1_6)
unnamed: SIM800L.P$2_VIN1 (P$2_VIN), SWITCH.L1, WIXEL.P$2 (P$2-VIN)
unnamed: SIM800L.P$8_DTR1 (P$8_DTR), WIXEL.P$16 (P$16-P1_3)

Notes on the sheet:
RPROG - IBAT (k) - (mA) 10 - 130 5 - 250 4 - 300 3 - 400 2 - 580 1.66 - 690 1.5 - 780 1.33 - 900 1.2 - 1000

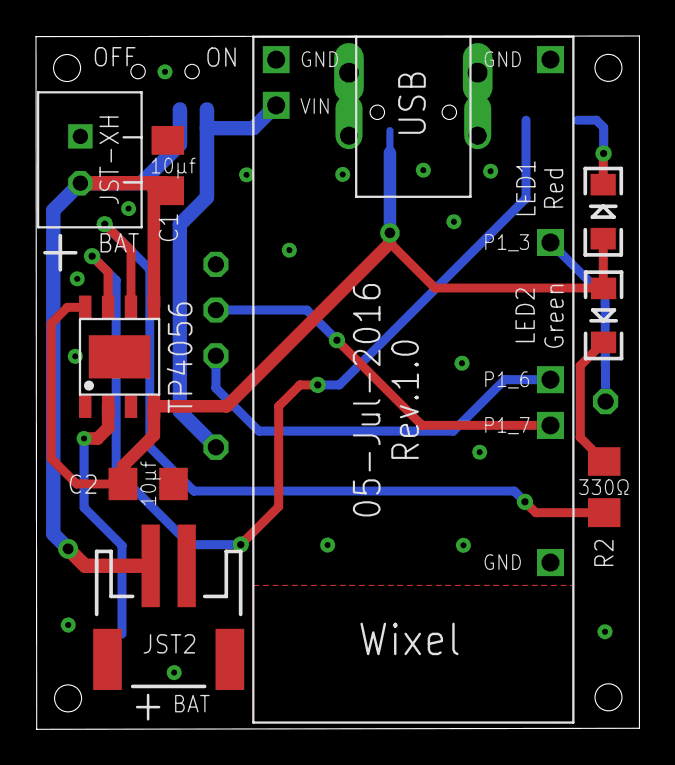
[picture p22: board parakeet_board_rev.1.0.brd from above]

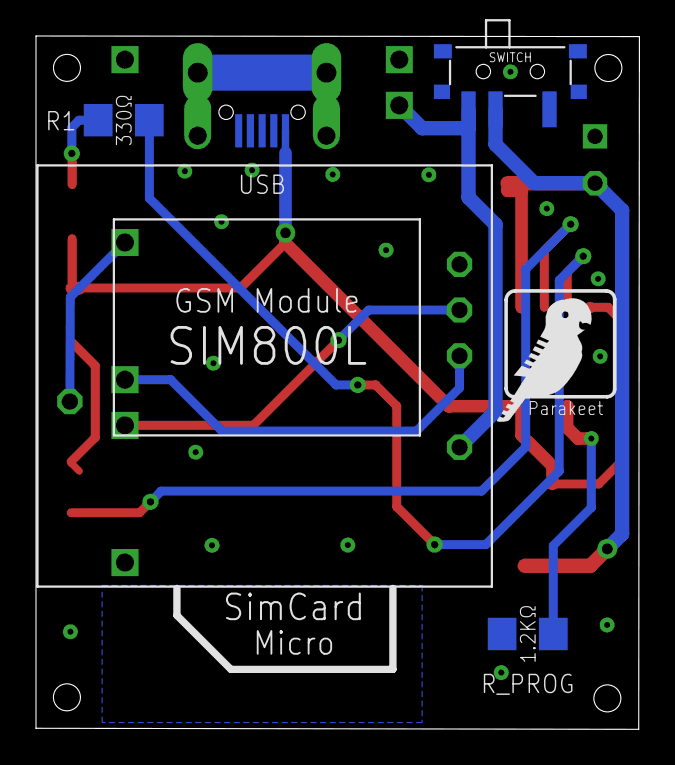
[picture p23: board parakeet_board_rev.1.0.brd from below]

Board: 2 copper layers, 33.5 x 38.5 mm, 15 parts (6 on the bottom side), 12 nets.

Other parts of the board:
U$2: PARAKEET

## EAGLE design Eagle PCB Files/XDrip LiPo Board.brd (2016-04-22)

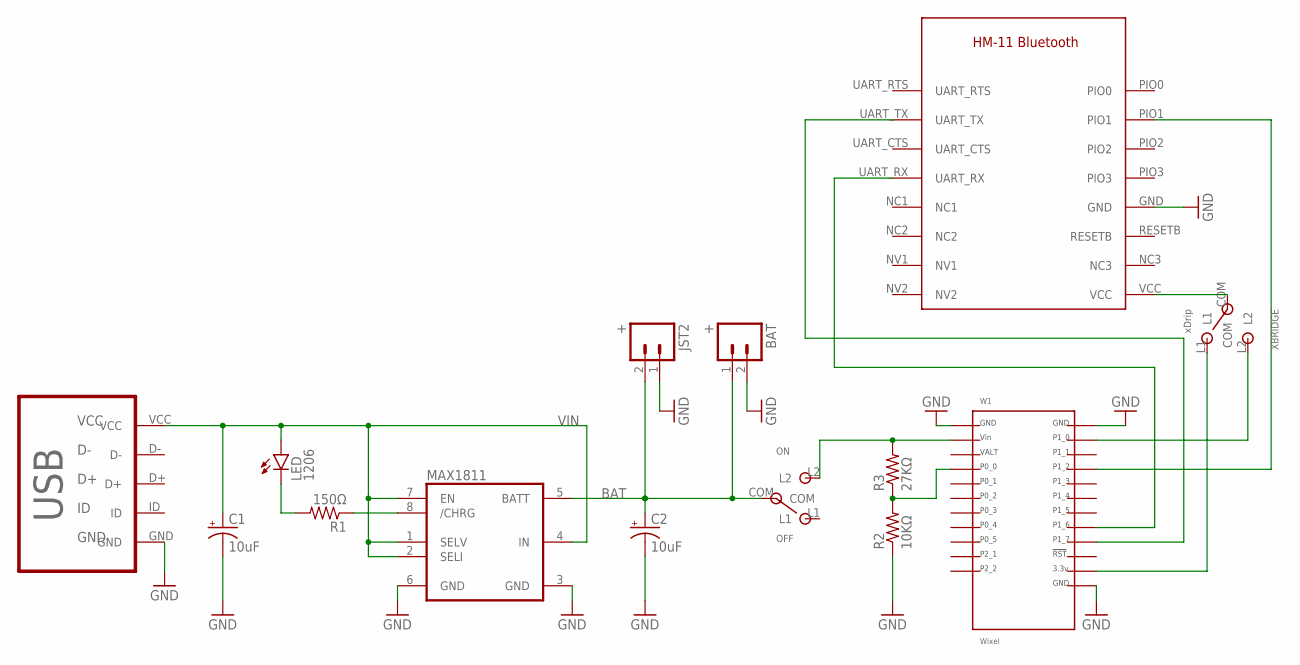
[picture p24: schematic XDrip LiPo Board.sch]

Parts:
BAT: +; 1X02
C1, C2: 10uF; EIA3216
JST2: +; JST-2-SMD
LED: 1206; LED-1206
MAX1811: MAX1811; SO08
ON: OFF; MSK-12C02
R1: 150Ω; 1206
R2: 10KΩ; 1206
R3: 27KΩ; 1206
U$2: HM-11
U$3: MICRO-USB-B; USB-AB-MICRO-SMD_V02_BOSS
W1: Wixel; WIXEL
XBRIDGE: xDrip; MSK-12C02

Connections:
BAT: BAT.1, C2.A (+), JST2.2 (1), MAX1811.5 (BATT), ON.COM
GND: BAT.2, C1.C (-), C2.C (-), JST2.1 (2), MAX1811.3 (GND), MAX1811.6 (GND), R2.1, U$2.GND, U$3.GND, W1.P$1, W1.P$12, W1.P$23
unnamed: U$2.VCC, XBRIDGE.COM
unnamed: LED.C, R1.2
unnamed: MAX1811.8 (/CHRG), R1.1
unnamed: ON.L2, R3.2, W1.P$2
unnamed: R2.2, R3.1, W1.P$4
unnamed: W1.P$13, XBRIDGE.L2
unnamed: U$2.PIO1, W1.P$15
unnamed: W1.P$22, XBRIDGE.L1
RX: U$2.UART_RX, W1.P$19
TX: U$2.UART_TX, W1.P$20
VIN: C1.A (+), LED.A, MAX1811.1 (SELV), MAX1811.2 (SELI), MAX1811.4 (IN), MAX1811.7 (EN), U$3.VCC

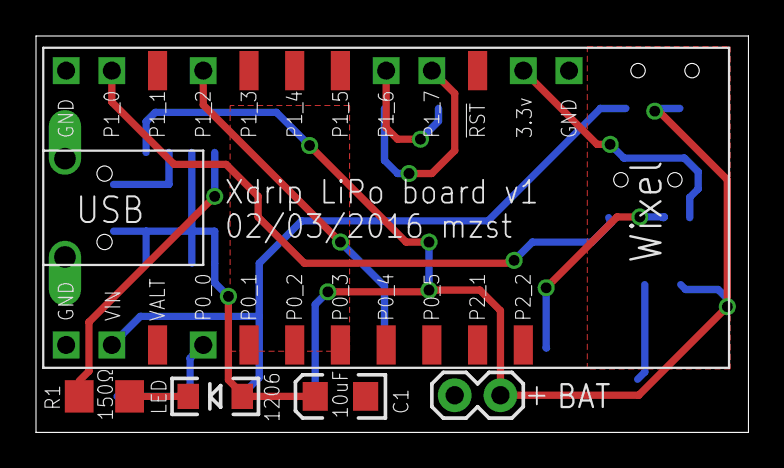
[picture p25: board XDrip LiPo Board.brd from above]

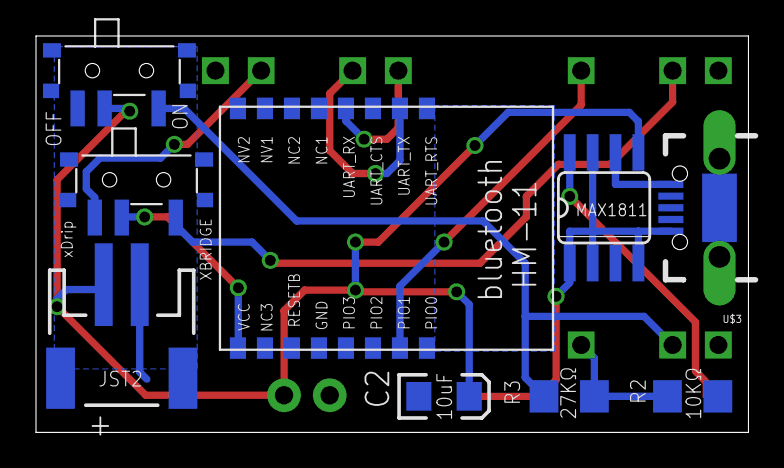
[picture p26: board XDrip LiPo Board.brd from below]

Board: 2 copper layers, 39.6 x 22.0 mm, 14 parts (9 on the bottom side), 13 nets.

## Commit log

2016-04-22 Summary
    Description
    [XDrip LiPo Board.brd, XDrip LiPo Board.sch]
2016-04-26 Added 3D Enclosure
    [BOTTOM.stl, TOP.stl]
2016-05-03 Updated Folder
    [XDrip LiPo Board.brd, XDrip LiPo Board.sch]
2016-05-03 Uploaded Fusion design files
    [Enclosure.f3d, Xdrip PCB.f3d, Xdrip PCB.stl]
2016-06-08 Added Parakeet Version
    [parakeet_board.brd, parakeet_board.sch]
2016-06-12 Updated GSM version
    [parakeet_board.brd, parakeet_board.sch]
2016-06-20 updated enclosure
    [BOTTOM.stl, Enclosure.f3d, TOP.stl, Xdrip PCB.f3d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]
2016-07-03 Updated Parakeet rev.09
    Fixed SIM800 module dimensions
    [parakeet_board_rev.09.brd, parakeet_board_rev.09.sch]
2016-07-05 updated parakeet version
    [parakeet_board_rev.1.0.brd, parakeet_board_rev.1.0.sch]
2016-07-13 Added 3D enclosure pictures

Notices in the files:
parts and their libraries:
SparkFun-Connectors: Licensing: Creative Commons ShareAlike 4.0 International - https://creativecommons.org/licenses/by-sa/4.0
